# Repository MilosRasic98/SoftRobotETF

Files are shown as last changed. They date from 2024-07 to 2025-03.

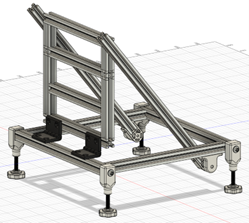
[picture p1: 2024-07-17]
Main Assembly/Frame/Pictures/FrameVertical.png

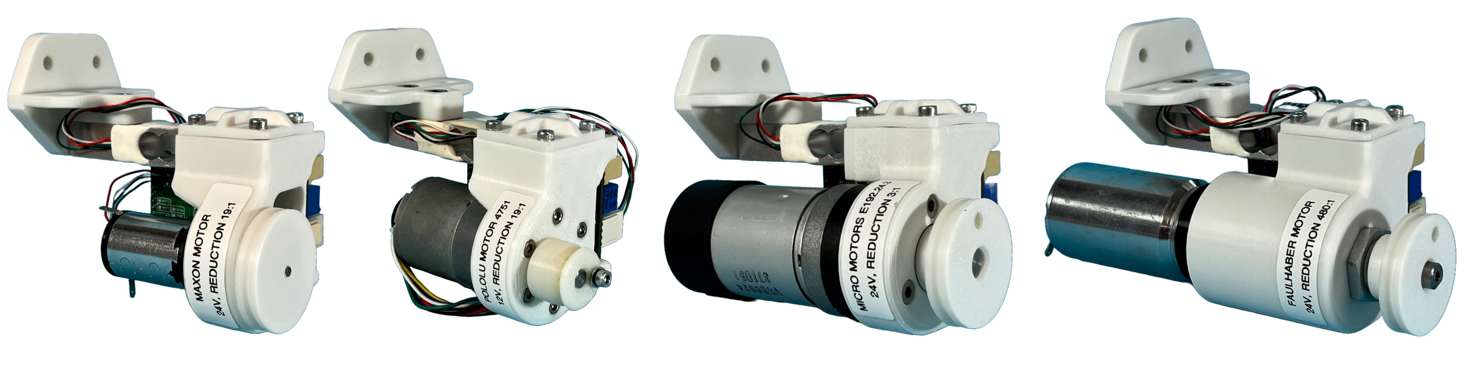
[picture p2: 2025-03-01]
Pictures/DifferentMotorSetups.png

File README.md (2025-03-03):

# Open Source Soft Robotics Platform - SoftRobotETF

This repository covers the complete development and testing of an open-source soft robotics platform developed at the School of Electrical Engineering, University of Belgrade in Serbia (https://www.etf.bg.ac.rs).

The main goal of this project was to develop a low-cost modular platform for testing different highly elastic soft robot continuum shapes and different actuator mechanisms. This platform was primarily used to test tendon-driven soft robots, both with internal and external tendon routing. This repository contains all of the necessary files for anyone to recreate this project. This includes:

1. Software for the Actuators, Robot Controller, and Python Scripts for controlling the Robot over Serial
2. Gerber files for the Actuator PCBs
3. CAD files for the actuators and the main soft robot construction
4. CAD files for 2 different silicone molds used for casting the soft robots

Besides this GitHub repository, there is a Google Sheet with the complete BOM for the Actuator PCB, known Errors, as well as the API and the implemented commands. You can find the sheet here: https://docs.google.com/spreadsheets/d/1j4l9SDbZnH_yYO-BC3xJZ4RkYJjM1L0_M2_zAHDFm0k/edit?usp=sharing

If you're trying to recreate a part of this project and you're stuck somewhere or some files are missing, feel free to contact me! Email: milosrasic98@gmail.com





To see how the robot looks in motion, click on the picture below, which will take you to the YouTube video, or click this link (https://www.youtube.com/watch?v=fuDRdF3EgcY)

IMAGE ALT TEXT HERE (https://www.youtube.com/watch?v=fuDRdF3EgcY)

## Requirement List

Before the development of this project, a requirement list was put together to guide the project in a single direction.

1. Ability to test different shapes and sizes of continuum shapes
2. Ability to test highly elastic soft robots
3. Precise force control tendon actuators
4. Multiple actuator setup

To satisfy the first two conditions, the frame of the robot was made using aluminium 20x20 extrustions. This enabled the maximum modularity and configurability of the system while still keeping everything sturdy. In this way, different actuators can be mounted using a few screws, and the same goes for different continuum shapes. 

Fig1_whitebackground_cropped

## Testing Different Shapes

To make the testing of different shapes even more straightforward, a plate and plate holder were designed and 3D printed so that different continuum shapes can easily be tested. In the pictures below, you can see the shape of the plate holder that attaches to the main frame. Soft robot bodies are cast with the plate attached to them and can then be easily attached to the plate holder with a couple of machine screws. This allows for easy testing of different continuum shapes by simply editing the CAD model of the plate to have the silicone anchors in the right places.

PlateWithDimensions

DifferentShapes

The plates shown above are designed for silicone continuums that are cast with the anchors inserted into the uncured silicone. Besides that, there are other options when using continuum shapes 3D printed out of TPU, for example. In the picure below, besides the silicone anchors, two additional methods can be seen for securing the continuum to the plate, one being with screws, and the other having a socket for glueing the continuum to the plate. 



## Testing Highly Elastic Soft Robots

While the shore hardness of the silicone above is high enough for the silicone robot to stand on its own in the vertical position, the idea with this platform was to enable testing silicone rubbers with lower shore hardnesses as well. For those cases, the silicone rubber wouldn't be able to support itself, so an addition to this platform is that the angle of the central part of the frame can be changed, and a simple holder for the silicone robot can be added, as shown in the picture below.

cropped_IMG_1597

## Actuators

A lot of time and effort was spent on the actuator design. The main goal for the actuators was, as stated above, to have precise force control. While current is directly proportional to the torque of the motor, the issue arises when the system needs to move from static to dynamic reference and vice versa, and also when there is a gearbox attached to the motor (sometimes with a lot of backlash). All of those things can cause issues with force control, which is why it was decided to measure the tendon force directly and close the control loop through the load cell measurement. The design of the final actuator is shown in the picture below.

ActuatorLabeledV2

A custom PCB was designed around the Raspberry Pi Pico as the MCU that controls a brushed DC motor using the DRV8842 motor driver. While a load cell is usually connected to an MCU using something like an HX711 24bit Sigma Delta ADC, this wasn't good enough for this use case since its maximum sample rate is 80SPS. Instead, the load cell was connected to an instrumentation amplifier, INA826, that could provide the necessary sample rate for the control loop. Since the amplification could be adjusted on the instrumentation amplifier using a potentiometer, a calibration method was needed to ensure accurate absolute measurements. This was done using a calibration stand that is described at the bottom of this Readme file. The gerber files for the PCB are available in the Actuators directory, and the PCB and electronics can be seen in the pictures below.

Outlook-PCB1 PNG

1-PowerElectronics

2-MotorController

3-LoadCell

4-RaspberryPico

The motors that are shown in all of the pictures above and that were used for all of the tests are the Pololu 12V motors with 19:1 reductors (https://www.pololu.com/product/2822). These aren't the motors that need to be used, however, because the design of the actuators allows the use of any brushed DC motor (Up to 28V and 5A) by redesigning a single 3D printable part. Different motor setups with the same electronics can be seen in the picture below.

DifferentMotorSetups

A single actuator can be used as a standalone unit by simply connecting a USB cable to the Raspberry Pi Pico. While this is easy to use for some simple tests, the goal was to be able to have multiple actuator setups. This is why both the hardware and software for these actuators were developed so that multiple of these actuators can be easily daisy-chained and controlled over I2C (Actuators have dual power connectors to enable daisy chaining, as well as multiple I2C connectors). In a multi-actuator setup, a Robot Controller Raspberry Pi Pico is needed that acts as the master device on the I2C bus.

The API for controlling the robot was designed to mimic the look of G Code commands, where a command number would be followed by space-separated parameters that are to be sent to the actuator(s). In a multi-actuator setup, these commands are sent to the Soft Robot Controller over Serial, which then translates those commands to I2C and sends them to all of the actuators. The Soft Robot Controller also plays a role in gathering the data from all of the actuators and from the IMU attached to the top of the robot. That data is saved into a CSV file and further analyzed after the tests are done. Some of the commands are shown in the table below

| Command | Name | Description | Command Format - Serial | Command Format - I2C | Parameters |
|---------|------|-------------|-------------------------|----------------------|------------|
| C0 | Stop All	| When the controller receives this command, it shuts down both PWM channels to 0% duty cycle, it disables the driver and turns off the enable LED | C0 | {0, 0, 0, 0, 0, 0, 0, 0, 0, 0, 0, 0, 0, 0, 0, 0} | None |
| C1 | Enable/Disable Driver (All) | When the controller receives this command, depending on the parameter, it will either enable or disable the driver, which will also be shown through the Enable LED on the PCB. Disabling the driver this way does not effect the PWM duty cycle like the C0 does |	C1 1/0 | {1, X, 0, 0, 0, 0, 0, 0, 0, 0, 0, 0, 0, 0, 0, 0} | X = 1 - Enable <br> X = 0 - Disable |
| C2 | Decay Mode | This command changes the decay mode on the DRV8842. For a detailed description of decay mode, refer to the datasheet of the DRV8842 motor driver. | C2 1/0 | {2, X, 0, 0, 0, 0, 0, 0, 0, 0, 0, 0, 0, 0, 0, 0} | X = 1 - Fast Decay <br> X = 0 - Slow Decay |
| C3 | Change Mode (All) | This command changes the mode of the actuator; in this way, the algorithm structure can be changed for the controller itself. <br> Mode 1 - Manual Control <br> Mode 2 - PI Controller Load Cell <br> Mode 3 - PI Controller IMU | C3 X | {3, X, 0, 0, 0, 0, 0, 0, 0, 0, 0, 0, 0, 0, 0, 0} | X - Mode X |
| C4 | Manual Drive | This command enables driving the motor in one or the other direction by setting the PWM duty cycle manually as well as the motor direction. For this command to work, the motor driver needs to be enabled first; the command will not automatically enable the motor driver. If the direction is set to 3, only the PWM will be changed with the before chosen direction. | C4 DX SY | {4, X, Y, 0, 0, 0, 0, 0, 0, 0, 0, 0, 0, 0, 0, 0} | X - Direction parameter [1, 2, 3] <br> X = 1 - Direction 1 <br> X = 2 - Direction 2 <br> X = 3 - Last direction <br> Y - Speed [0 - 100] <br> Y = Duty Cycle [%] |
| C5 | Set Force Reference | This command sets the reference of the PI Controller that closes its loop through the load cell. The reference is set in grams and can be anything between 0g and 10000g (0g to 1000g in safe mode). For I2C, the reference is calculated as: <br> Reference = 255 * X1 + X2 | C5 X | {5, X1, X2, 0, 0, 0, 0, 0, 0, 0, 0, 0, 0, 0, 0, 0} | X - Force reference [0-10000] <br> X = X1 * 255 + X2 |

The table above shows some of the commands. The full list of commands and future commands that will be added can be found in the Google Sheet: https://docs.google.com/spreadsheets/d/1j4l9SDbZnH_yYO-BC3xJZ4RkYJjM1L0_M2_zAHDFm0k/edit?usp=sharing

## Silicone Rubber

In the pictures above, two different silicone rubbers are shown. The pink silicone rubber is Mold Max 30 silicone (https://www.smooth-on.com/products/mold-max-30/), which was mixed as per the manufacturer's instructions and degassed in a vacuum chamber before being poured into a mold. The green silicone rubber was an experiment using natural silicone rubber mixed with food dye to speed up the curing process before being poured into the mold. For testing the properties of the different silicones, a manual strain test apparatus was constructed for measuring the tensile strength of the different silicone rubbers.



Results that were made using this apparatus are shown in the two figures below.

Silicone Rubber - Sample 1

Silicone Rubber - Force Change at 100 Elongation

CAD models for both of the molds can be found in the CAD directory. Since the plate had to stay attached to the silicone after taking it out of the mold. Special consideration was taken in designing these molds so that they can be disassembled around the soft robot, leaving the soft robot with the plates attached in the end.

ExplodedMold2

MoldFigureEdited

## Test Stand

As mentioned above, the actuator needs to be calibrated because the amplification of the instrumentation amplifier can be adjusted using a potentiometer. The calibration stand has a calibrated load cell at the top that is connected to the actuator using a tensioner and a spring. In this way, the force can be adjusted and kept at the desired force. The calibration stand and the calibration graph are shown in the pictures below.

CalibrationStand

Actuator Load Cell Calibration

## Results

This part will showcase some of the recorded results using this setup. The results shown here are with either one or two actuators, with an MPU6050 attached to the top of the robot. The measurements are done on the round Mold Max 30 silicone continuum. In the picture below, a sawtooth reference was sent to the actuator between 10N and 50N. This soft robot had internally routed tendons.

Reference Measurement - Test Segment - Sawtooth

The angle measured at the top of the robot is shown in the figure below.

Roll Angle - Test Segment - Sawtooth

By looking at a rising edge of the single peak, we can try estimating a linear function to approximate the angle based on the force, as shown in the picture below.

Angle Estimation Based on Force - Segment

Using the parameters of those lines, the comparison between the measured and estimated angles is shown in the figure below.

Roll Angle Measured and Estimated - Test Segment - Sawtooth

Using the parameters from the line calculated above, the estimated angle was calculated for a test where a sine reference was sent to the actuator.

Roll Angle Measured and Estimated - Full Test - Sine

The estimations weren't done for the two-actuator setup because there is coupling between the actuators; the actuators were placed at 90 degrees from each other. The results of those tests are shown below.

Reference Measurement - Test Segment

Pitch and Roll - Test Segment

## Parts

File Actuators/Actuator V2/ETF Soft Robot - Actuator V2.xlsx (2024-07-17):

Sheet: Document Outline
Document Description: |  |  | This document contains all of the relevant information needed for developing, testing and using the Soft Robot V1, as well as all of the relevant documentation like the BOM and the Pico Pinout. This document consists of multiple tabs, this first tab is used to outline the whole document as well as give a description of all tabs that are in this document.
Document Author: |  | Milos Rasic
Author Email: |  | milosrasic98@gmail.com
Table of Contents |  |  |  | Warnings
# | Tab Name | Tab Description |  | # | Name | Description
1 | PCB V1 Parts Sourcing | This tab contains the BOM for the PCB V1 as well as the designators for all components and locations where to buy them (if possible, Kelco was chosen as a supplier since they are local, if not, Farnell was used) |  | 1 | Low Number Command Checks | Because the inital version of the code checks the command code based on what it starts with, there is a possibility of treating a command like C10 for a C1 command, make sure that the character after the command code is a space.
2 | Error Log List | Error Log List contains the list of all errors that were noticed during soldering as well testing of the new PCB. This is also a place where new features or ideas can be written down for next iterations. |  | 2
3 | Pico Pinout | Pico Pinout contains a spreadsheet with connections for all of the pins on the Raspberry Pico as well as status for all of the pins have been they tested or not. |  | 3
4 | Commands | This tab contains the list of commands that can be used with the Soft Robot Controller, it includes their description, variants both for Serial and I2C communication, as well as examples and parameters descriptions. |  | 4
5 | LED Reading Manual | This tab shows how to read the different signals given by the LEDs on the actuator |  | 5
6 | Actuator Calibartion | All of the collected measurements used for getting values in grams from raw ADC values |  | 6
7 | Actuator Info | Contains all of the relevant info and parameters for each of the actuators |  | 7
8 | Wiring Diagrams | All of the important wiring diagrams which need additional clarification |  | 8
9 |  |  |  | 9
10 |  |  |  | 10
11 |  |  |  | 11
12 |  |  |  | 12
13 |  |  |  | 13
14 |  |  |  | 14
15 |  |  |  | 15
16 |  |  |  | 16
17 |  |  |  | 17
18 |  |  |  | 18
19 |  |  |  | 19
20 |  |  |  | 20

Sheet: PCB V1 Parts Sourcing
Tab Description: |  | This tab represents the BOM for the PCB V1, it includes numbers needed for each PCB as well as the designators, besides that each part is linked at least to one store, if possible, parts were sourced from Kelco since they are the local supplier with the biggest inventory of SMD components, while for most other things, the chosen supplier was Farnell.
# | Name | Designator | Store | Qty per Board | Description | Alternative | Link | Part of Circuit | Number Ordered | Status | ID
1 | TSP54331DR | U6 | Farnell | 1 | Buck Chip | X | https://export.farnell.com/texas-instruments/tps54331dr/dc-dc-conv-buck-570khz-soic-8/dp/3121757?st=buck | Power Supply | 3+3 | Arrived | SMD-B2-R2C1
2 | SDR0604-6R8ML | D1 | Farnell | 1 | Power Inductor | X | https://export.farnell.com/bourns/sdr0604-6r8ml/inductor-6-8uh-2-5a-smd/dp/1828001 | Power Supply | 5+5 | Arrived | SMD-B2-R1C1
3 | B340A-13-F | D2, D3 | Farnell | 2 | Schottky Diode | X | https://export.farnell.com/multicomp-pro/b340a-13-f/diode-rectifier-3a-40v-do-214ac/dp/2306401?st=b340a | Power Supply | 10 | Arrived | SMD-B1-R3C5
4 | 08056D476MAT2A | C1, C2, C3, C10, C20, C21 | Farnell | 6 | 4.7uF Cap | X | https://export.farnell.com/kyocera-avx/08056d476mat2a/cap-47uf-6-3v-x5r-0805/dp/4164100 | All Schematics | 30 | Arrived | SMD-B1-R1C5
5 | MCWR06X2942FTL | R1 | Farnell | 1 | 29k4 Resistor | X | https://export.farnell.com/multicomp/mcwr06x2942ftl/res-29k4-1-0-1w-0603-thick-film/dp/2694813 | Power Supply | 20 | Arrived | SMD-B1-R2C6
6 | 100nF Cap | C4, C6, C7, C11, C13, C16, C17, C18, C19, C22, C23 | Kelco | 11 | 100nF Cap 0603 | X | https://kelco.rs/katalog/detalji.php?ID=11061 | All Schematics | 100 | Arrived | SMD-B1-R1C4
7 | 10nF Cap | C5, C12 | Kelco | 2 | 10nF Cap 0603 | X | https://kelco.rs/katalog/detalji.php?ID=11586 | All Schematics | 100 | Arrived | SMD-B1-R1C3
8 | 1nF Cap | C8 | Kelco | 1 | 1nF Cap 0603 | X | https://kelco.rs/katalog/detalji.php?ID=10781 | Power Supply | 100 | Arrived | SMD-B1-R1C2
9 | 47pF Cap | C9 | Kelco | 1 | 47pF Cap | X | https://kelco.rs/katalog/detalji.php?ID=12902 | Power Supply | 100 | Arrived | SMD-B1-R1C1
10 | 15k Resistor | R2, R4, R5 | Kelco | 3 | 15k Resistor | X | https://kelco.rs/katalog/detalji.php?ID=13740 | All Schematics | 100 | Arrived | SMD-B1-R2C5
11 | 4k7 Resistor | R3, R16, R17, R22, R23 | Kelco | 5 | 4k7 Resistor | X | https://kelco.rs/katalog/detalji.php?ID=11708 | All Schematics | 100 | Arrived | SMD-B1-R2C3
12 | DRV8842 | U5 | Farnell | 1 | DC Motor Driver | X | https://export.farnell.com/texas-instruments/drv8842pwp/stepper-motor-driver-5a-28htssop/dp/3005858?st=dc%20motor%20driver | Motor Driver | 3+3 | Arrived | SMD-B2-R2C2
13 | WW06PR750FTL | R9, R10, R11, R12, R13 | Farnell | 5 | Current Sense Resistor | X | https://export.farnell.com/walsin/ww06pr750ftl/res-0r75-1-50v-0603-thick-film/dp/2503092 | Motor Driver | 30 | Arrived | SMD-B1-R2C1
14 | 2850090 | F1 | Farnell | 1 | Fuse 5A | Fuse 2A | https://export.farnell.com/multicomp/mccfb2410ttt-c-5/fuse-smd-5a-slow-blow-2410/dp/2850090 | Power Supply | 2+5 | Arrived | SMD-B2-R1C7
15 | INA826 | U7 | Farnell | 1 | Instrumentation Amp | X | https://export.farnell.com/texas-instruments/ina826aidgk/ic-amp-instr-8msop/dp/3004514 | Sense Circuit | 2+3 | Arrived | SMD-B1-R2C3
16 | 680R 0603 | R18, R19, R20, R21, R24 | Kelco | 5 | 680R 0603 - LED Resistor | X | https://kelco.rs/katalog/detalji.php?ID=14179 | All Schematics | 100 | Arrived | SMD-B1-R2C2
17 | 5k6 0603 | R6, R7 | Kelco | 2 | 5k6 0603 Resistor | X | https://kelco.rs/katalog/detalji.php?ID=11709 | Motor Driver | 100 | Arrived | SMD-B1-R2C4
18 | 1M 0603 | R8 | Kelco | 1 | 1M 0603 Resistor | X | https://kelco.rs/katalog/detalji.php?ID=13744 | Motor Driver | 10 | Arrived | SMD-B1-R2C7
19 | 100uF Electrolytic Cap | C14, C15 | Kelco | 2 | 100uF Electrolytic Cap | X | https://kelco.rs/katalog/detalji.php?ID=9985 | All Schematics | 15 | Arrived | ALL-B3-R1C3
20 | Trim Pot 100R | R14, R15 | Kelco | 2 | Trim Pot 100R | X | https://kelco.rs/katalog/detalji.php?ID=9990 | Sense Circuit | 10 | Arrived | ALL-B3-R1C4
21 | Trim Pot 20R |  | TODO |  | Trim Pot 20R | X | TODO |  | 10 | Need to Buy | ALL-B3-R1C5
22 | Red LED | LED1, LED2, LED3, LED4, LED5, LED6 | Kelco | 6 | Red LED 0603 | X | https://kelco.rs/katalog/detalji.php?ID=18012 | All Schematics | 20 | Arrived | SMD-B1-R3C1
23 | Green LED |  | Kelco |  | Green LED 06033 | X | https://kelco.rs/katalog/detalji.php?ID=18013 | All Schematics | 20 | Arrived | SMD-B1-R3C2
24 | Blue LED |  | Kelco |  | Blue LED 0603 | X | https://kelco.rs/katalog/detalji.php?ID=17592 | All Schematics | 10 | Arrived | SMD-B1-R3C3
25 | Pink LED |  | Kelco |  | Pink LED 0603 | X | https://kelco.rs/katalog/detalji.php?ID=17568 | All Schematics | 10 | Arrived | SMD-B1-R3C4
26 | Power Connector PCB | J1, J2 | Kelco | 2 | Power Connector PCB | X | https://kelco.rs/katalog/detalji.php?ID=12651 | Power Supply | 10 | Arrived | ALL-B3-R1C1
27 | Power Connector Cable |  | Kelco |  | Power Connector Cable | X | https://kelco.rs/katalog/detalji.php?ID=12721 | Power Supply | 4 | Arrived | ALL-B3-R1C2
28 | Raspberry Pico | MCU1 | Farnell | 1 | Raspberry Pico Microcontroller | Raspberry Pico W | https://export.farnell.com/raspberry-pi/raspberry-pi-pico/raspberry-pi-32bit-arm-cortex/dp/3643332 | Microcontroller | 2 | Arrived | ALL-B3-R2C1
29 | Female Headers 2.54 | PIN1 | Kelco | X | Female header pins | X | https://kelco.rs/katalog/detalji.php?ID=18882 | All Schematics | 10 | Arrived | ALL-B3-R3C1
30 | Male Header 2.54 | PIN2 | Kelco | X | Male header pins | X | https://kelco.rs/katalog/detalji.php?ID=7923 | All Schematics | 3 | Arrived | ALL-B3-R3C2
31 | Nylon Connector 4P PCB | NYL1, NYL2, NYL3, NYL4, NYL5 | Kelco | 5 | Nylon Connector 4P PCB | X | https://kelco.rs/katalog/detalji.php?ID=7918 | All Schematics | X | In Stock | ALL-B3-R2C4
32 | Nylon Connector 4P Cable |  | Kelco |  | Nylon Connector 4P Cable | X | https://kelco.rs/katalog/detalji.php?ID=7913 |  | X | In Stock | ALL-B3-R1C6
33 | Nylon Connector Pins |  | Kelco |  | Nylon Connector Pins | X | https://kelco.rs/katalog/detalji.php?ID=14868 |  | X | In Stock | TODO
34 | INA125P | U1 | Kelco | 1 | Instrumentation Amp | X | https://kelco.rs/katalog/detalji.php?ID=21799 | Sense Circuit | X | Need to Buy | TODO
35 | DIP16 Socket | U1_SOCKET | Kelco | 1 | Socket for DIP16 | X | TODO | Sense Circuit | X | Need to Buy | ALL-B3-R2C2
36 | Male Header 2x2.54 | PIN3 | Kelco | X | Pins for the jumpers | X | https://kelco.rs/katalog/detalji.php?ID=10308 | All Schematics | X | Need to Buy | ALL-B3-R2C3
37 | Jumpers | PIN4 | Kelco | X | Jumpers for selecting settings | X | https://kelco.rs/katalog/detalji.php?ID=16633 | All Schematics | X | Need to Buy | TODO
38
39
40
41
42
43
44
45
46
47
48
49
50

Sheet: Error Log List
Tab Description: |  | This tab represents the Error and Idea log that will be updated through the development and the testing process.
# | Error Name | Error Type | Error/Idea Description | Proposed Solution | Board Version | Date | Importance | Urgency | Status
1 | Inductor Footprint | PCB | The footprint that was used for the inductor is too small. | Either correct the footprint on the PCB, or if possible, find an alternative inductor that has the matching footprint to the current one. | V1 | 17.12.2023 | Critical | Non Urgent | Not Solved
2 | Electrolyric Cap Footprint | PCB | The footprint that was used for the eletrolytic capacitor is a bit on the smaller side making it hard to solder the capacitor properly to the PCB. | Try using a smaller capactior (smaller ones are just rated to a lower voltage, the current one is rated up to 50V), or use a different footprint for the capacitor. | V1 | 17.12.2023. | Non Critical | Non Urgent | Not Solved
3 | 3V3 LED too bright | Schematic | The 3V. power LED is too bright when used with a 680R resistor. | Try using 1k-2k until the desired brightness is achieved | V1 | 17.12.2023. | Non Critical | Non Urgent | Not Solved
4 | Silkscreen missmatch C10 | PCB | Silkscreen on the PCB for C10 and C11 have been swapped around | Fix the silk screen in EasyEDA | V1 | 17.12.2023. | Non Critical | Non Urgent | Not Solved
5 | Pico Caps to bottom | PCB | Capacitors used for the Raspberry Pico are too close to the female box connected of the Raspberry Pico. | There is a lot of space underneath the pico (bottom layer), move the capacitors to the bottom layer to make the soldering easier | V1 | 17.12.2023. | Non Critical | Non Urgent | Not Solved
6 | Encoder divider resistors to bottom | PCB | The voltage divider resistors used for the encoder are underneath the Pico on the top layer, making them hard to solder and work on once the Pico is in place. | Consider moving the resistors to the bottom layer if there is enough room for tracks. | V1 | 17.12.2023. | Non Critical | Non Urgent | Not Solved
7 | PCB ID | Idea / Feature | Distinguish between different PCB-s within the same batch. | Add a silkscreen place (rectangle or something similar) where a sticker could be put with the ID of the PCB. | V1 | 17.12.2023. | Non Critical | Non Urgent | Not Solved
8 | I2C Address | Idea / Feature | Physical way of changing the I2C address on the Raspberry Pico | Add a DIP switch to easily change the I2C address on each PCB | V1 | 17.12.2023. | Non Critical | Non Urgent | Not Solved
9
10
11
12
13
14
15
16
17
18
19
20
21
22
23
24
25
26
27
28
29
30
31
32
33
34
35
36
37
38
39
40
41
42
43
44
45
46
47
48
49
50
51
52
53
54
55
56
57
58
59
60
61
62
63
64
65
66
67
68
69
70
71
72
73
74
75
76
77
78
79
80
81
82
83
84
85
86
87
88
89
90
91
92
93
94
95
96
97
98
99
100

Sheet: Pico Pinout
Tab Description: |  | This tab represents the pinout of the Pico and how it's connected to everything on the PCB V1, it shows all of the pins, the connections as well as if that pin feature has been tested/implemented yet.
Status | Pin Purpose | Pin Connection | GPIO | Pin Number | Pin Number | GPIO | Pin Connection | Pin Purpose | Status
Unused | NC | NC | GPIO0 | 1 | 40 | X | NC | NC | Unused
Unused | NC | NC | GPIO1 | 2 | 39 | X | NC | NC | Unused
Done | GND | GND | GND | 3 | 38 | GND | GND | GND | Done
Needs Testing | PWM for controlling the spin of the motor in one direction | MOTOR_CTRL_1 | GPIO2 | 4 | 37 | X | NC | NC | Unused
Needs Testing | Changes the decay mode for the DRV8842, HIGH is fast decay, LOW is slow decay | MOTOR_DECAY | GPIO3 | 5 | 36 | X | 3V3 | Input Power from buck - 3V3 | Done
Needs Testing | PWM for controlling the spin of the motor in the other direction | MOTOR_CTRL_2 | GPIO4 | 6 | 35 | X | NC | NC | Unused
Needs Testing | Fault signal from the motor driver | MOTOR_FAULT | GPIO5 | 7 | 34 | GPIO28 | LOAD_CELL_INA826 | Input signal from the load cell that is connected to the INA826 | Needs Testing
Done | GND | GND | GND | 8 | 33 | GND | GND | GND | Done
Needs Testing | Signal for putting the motor driver to sleep | MOTOR_SLEEP | GPIO6 | 9 | 32 | GPIO27 | LOAD_CELL_INA125 | Input signal from the load cell that is connected to the INA125 | Needs Testing
Needs Testing | Signal for reseting the motor driver | MOTOR_RESET | GPIO7 | 10 | 31 | GPIO26 | MOTOR_CURRENT | Input analog signal from the motor driver for measuring the current consumption of the motor | Needs Testing
Done | Signal for the Heartbeat LED, pulses at 1Hz in normal operation, in error state switches to 5Hz | LED_HEARTBEAT | GPIO8 | 11 | 30 | X | NC | NC | Unused
Unused | Encoder A input signal from the motor | ENC_A | GPIO9 | 12 | 29 | GPIO22 | GPIO_22 | Not used | Unused
Done | GND | GND | GND | 13 | 28 | GND | GND | GND | Done
Unused | Encoder B input signal from the motor | ENC_B | GPIO10 | 14 | 27 | GPIO21 | I2C_SCL | I2C communication with the master controller | Needs Testing
Done | Signal for the Fault LED which shows if there is a fault reported by the motor driver | LED_DRV_FAULT | GPIO11 | 15 | 26 | GPIO20 | I2C_SDA | I2C communication with the master controller | Needs Testing
Done | Signal for the Enable LED, this LED shows if the power electronics have been enabled for the motor | LED_DRV_EN | GPIO12 | 16 | 25 | GPIO19 | SPI0_MOSI | Not used | Unused
Done | Signal for the Mode LED, which shows which type of software driver is currently enabled, can be configured for anything else as well | LED_CTRL_MODE | GPIO13 | 17 | 24 | GPIO18 | SPI0_CLK | Not used | Unused
Done | GND | GND | GND | 18 | 23 | GND | GND | GND | Done
Needs Testing | Connection to the HX711 for the calibration stand | HX711_SCK | GPIO14 | 19 | 22 | GPIO17 | SPI0_CSN | Not used | Unused
Needs Testing | Connection to the HX711 for the calibration stand | HX711_DT | GPIO15 | 20 | 21 | GPIO16 | SPI0_MISO | Not used | Unused
Legend
Done | Everything works as expected
Needs Testing | Still not tested and implemented
Unused | Not used for now, needs testing before use
Not Working | Testing failed

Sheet: Commands
Tab Description: |  | This tab represents all of the commands that can be used with the Soft Robot Actuator as well as their formats, descriptions, examples and parameters descriptions.
# | Command Code | Name | Description | Command Format - Serial | Command Example - Serial | Command Format - I2C | Command Example - I2C | Parameters | Status
0 | C0 | Stop All | When the controller receives this command, it shuts down both PWM channels to 0% duty cycle, it disables the driver and turns off the enable LED | C0 | C0 | {0, 0, 0, 0, 0, 0, 0, 0, 0, 0, 0, 0, 0, 0, 0, 0} | {0, 0, 0, 0, 0, 0, 0, 0, 0, 0, 0, 0, 0, 0, 0, 0} | None | Done
1 | C1 | Enable/Disable Driver | When the controller receives this command, depending on the parameter, it will either enable or disable the driver, which will also be shown through the Enable LED on the PCB. Disabling the driver this way does not effect the PWM duty cycle like the C0 does | C1 1/0 | C1 1 - Enable Driver C1 0 - Disable Driver | {1, X, 0, 0, 0, 0, 0, 0, 0, 0, 0, 0, 0, 0, 0, 0} | {1, 1, 0, 0, 0, 0, 0, 0, 0, 0, 0, 0, 0, 0, 0, 0} - Enable {1, 0, 0, 0, 0, 0, 0, 0, 0, 0, 0, 0, 0, 0, 0, 0} - Disable | X = 1 - Enable X = 0 - Disable | Done
2 | C2 | Decay Mode | This command changes the decay mode on the DRV8842. For a detailed description of decay mode refer to the datasheet of the DRV8842 motor driver. | C2 1/0 | C2 1 - Fast Decay Mode C2 0 - Slow Decay Mode | {2, X, 0, 0, 0, 0, 0, 0, 0, 0, 0, 0, 0, 0, 0, 0} | {2, 1, 0, 0, 0, 0, 0, 0, 0, 0, 0, 0, 0, 0, 0, 0} - Fast Decay {2, 0, 0, 0, 0, 0, 0, 0, 0, 0, 0, 0, 0, 0, 0, 0} - Slow Decay | X = 1 - Fast Decay X = 0 - Slow Decay | Done
3 | C3 | Change Mode | This command changes the "mode" of the actuator, in this way, algorithm structure can be changed for the controller itself. Mode 1 - Manual Control Mode 2 - PI Controller Load Cell Mode 3 - PI Controller IMU | C3 X | C3 1 - Switch to Mode 1 C3 2 - Switch to Mode 2 | {3, X, 0, 0, 0, 0, 0, 0, 0, 0, 0, 0, 0, 0, 0, 0} | {3, 1, 0, 0, 0, 0, 0, 0, 0, 0, 0, 0, 0, 0, 0, 0} - Mode 1 {3, 2, 0, 0, 0, 0, 0, 0, 0, 0, 0, 0, 0, 0, 0, 0} - Mode 2 | X - Mode X | Done
4 | C4 | Manual Drive | This command enables driving the motor in one or the other direction by setting the PWM duty cycle manually as well as the motor direction. For this command to work, the motor driver needs to be enabled first, the command will not automatically enable the motor driver. If the direction is set to 3, only the PWM will be changed with the before chosen direction. | C4 DX SY | C4 D1 S50 - Direction 1 Speed 50 C4 D2 S90 - Direction 2 Speed 90 | {4, X, Y, 0, 0, 0, 0, 0, 0, 0, 0, 0, 0, 0, 0, 0} | {4, 1, 50, 0, 0, 0, 0, 0, 0, 0, 0, 0, 0, 0, 0, 0} - Dir 1 Speed 50 {4, 2, 90, 0, 0, 0, 0, 0, 0, 0, 0, 0, 0, 0, 0, 0} - Dir 0 Speed 90 | X - Direction parameter [1, 2, 3] X = 1 - Direction 1 X = 2 - Direction 2 X = 3 - Last direction Y - Speed [0 - 100] Y = Duty Cycle [%] | Done
5 | C5 | Set Force Reference | This command sets the reference of the PI Controller that closes its loop through the load cell. The reference is set in grams and can be anything between 0g and 10000g (0g to 1000g in safe mode). For I2C, the reference is calculated as Reference = 255 * X1 + X2 | C5 X | C5 1250 - Set reference to 1250g | {5, X1, X2, 0, 0, 0, 0, 0, 0, 0, 0, 0, 0, 0, 0, 0} | {5, 4, 230, 0, 0, 0, 0, 0, 0, 0, 0, 0, 0, 0, 0, 0} - Set reference to 1250g | X - Force reference [0-10000] X = X1 * 255 + X2 | Done
6 | C6 | Reset Force Controller | This command resets the accumulator of the load cell PI controller. | C6 | C6 | {6, 0, 0, 0, 0, 0, 0, 0, 0, 0, 0, 0, 0, 0, 0, 0} | {6, 0, 0, 0, 0, 0, 0, 0, 0, 0, 0, 0, 0, 0, 0, 0} | None | Need to Implement
7 | C7 | Safe Mode | This puts the whole controller into Safe Mode, which limits the PWM to 25% duty cycle, it also puts a limit on the reference of 1000g and enables safe mode failsafe, that shuts down the driver if the load cell is detected to be over 1000g. | C7 | C7 | {7, 0, 0, 0, 0, 0, 0, 0, 0, 0, 0, 0, 0, 0, 0, 0} | {7, 0, 0, 0, 0, 0, 0, 0, 0, 0, 0, 0, 0, 0, 0, 0} | None | Need to Implement
8 | C8 | Save Parameters | Save all of the editable parameters to the flash memory of the Pico | C8 | C8 | {8, 0, 0, 0, 0, 0, 0, 0, 0, 0, 0, 0, 0, 0, 0, 0} | {8, 0, 0, 0, 0, 0, 0, 0, 0, 0, 0, 0, 0, 0, 0, 0} | None | Research
9 | C9 | Change Force Controller Parameters | With this command, change the Kp and Ki parameters of the load cell PI controller | C9 KP KI | C9 0.1 0.005 | TODO | TODO | TODO | Research
10 | C10 | Reset All Errors | Using this command, reset any errors that have happened on the controller | C10 | C10 | {10, 0, 0, 0, 0, 0, 0, 0, 0, 0, 0, 0, 0, 0, 0, 0} | {10, 0, 0, 0, 0, 0, 0, 0, 0, 0, 0, 0, 0, 0, 0, 0} | None | Done
11 | C11 | Enable/Disable Overcurrent Protection | Through current sense resistors, the DRV8842 can measure current and the Pico reads that using an analog pin. This command can enable or disable the overcurrent protection. If the overcurrent protection is enabled and the measured current goes above the overcurrent protection limit, the Pico will disable the driver, kill the PWM and go into error state. | C11 1/0 | C11 1 - Enable OC C11 0 - Disable OC | {11, X, 0, 0, 0, 0, 0, 0, 0, 0, 0, 0, 0, 0, 0, 0} | {11, 1, 0, 0, 0, 0, 0, 0, 0, 0, 0, 0, 0, 0, 0, 0} - Enable OC {11, 0, 0, 0, 0, 0, 0, 0, 0, 0, 0, 0, 0, 0, 0, 0} - Disable OC | X = 1 - Enable OC X = 0 - Disable OC | Need to Implement
12 | C12 | Set Overcurrent Protection Limit | Set the limit in mA at which the OC protection is triggered. This value can go anywhere from 0 to 3000mA, keep in mind the strength of the fuse that is currently installed on the PCB | C12 X | C12 1250 - Set OC limit at 1250mA | {12, X1, X2, 0, 0, 0, 0, 0, 0, 0, 0, 0, 0, 0, 0, 0} | {12, 4, 230, 0, 0, 0, 0, 0, 0, 0, 0, 0, 0, 0, 0, 0} - Set OC limit at 1250mA | X - OC Current Limit [0-3000] X = X1 * 255 + X2 | Need to Implement
13 | C13 | Live Serial Data | Toggle the live stream of all of the measured data on the actuator using this command, the only argument for the command is 1/0 that let's the user either enable or disable the data stream. | C13 1/0 | C13 1 - Enable Serial Data Stream C13 0 - Disable Serial Data Stream | {13, X, 0, 0, 0, 0, 0, 0, 0, 0, 0, 0, 0, 0, 0, 0} | {13, 1, 0, 0, 0, 0, 0, 0, 0, 0, 0, 0, 0, 0, 0, 0} - Enable {13, 0, 0, 0, 0, 0, 0, 0, 0, 0, 0, 0, 0, 0, 0, 0} - Disable | X = 1 - Enable X = 0 - Disable | Need to Implement
14 | C14
15 | C15
16 | C16
17 | C17
18 | C18
19 | C19
20 | C20
21 | C21
22 | C22
23 | C23
24 | C24
25 | C25
26 | C26
27 | C27
28 | C28
29 | C29
30 | C30
31 | C31
32 | C32
33 | C33
34 | C34
35 | C35
36 | C36
37 | C37
38 | C38
39 | C39
40 | C40
41 | C41
42 | C42
43 | C43
44 | C44
45 | C45
46 | C46
47 | C47
48 | C48
49 | C49
50 | C50

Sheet: LED Reading Manual
Tab Description: |  | This tab represents the BOM for the PCB V1, it includes numbers needed for each PCB as well as the designators, besides that each part is linked at least to one store, if possible, parts were sourced from Kelco since they are the local supplier with the biggest inventory of SMD components, while for most other things, the chosen supplier was Farnell.
# | LED Name | LED Description | Reading Manual | Troubleshooting
1 | 12V | The 12V LED indicates if the 12V power is coming to the board (after fuse). | If the LED is ON that means that 12V is coming into the system, if it's OFF that means that 12V is not coming into the system. | If the LED is OFF and you think it should be ON (Turned on PSU, everything connected), check if the fuse is okay, after that check the actual voltage on the board with the mutlimeter.
2 | 3V3 | The 3V3 LED indicated if the 3V3 rail is at a 3.3V level. | If the LED is ON, there is power on the 3V3 rail, if it's OFF there is no power on the 3V3 rail. | 3V3 LED can be ON and the 12V OFF only if the board is getting power from either the USB cable or from one of the I2C connectors. If the 3V3 LED is OFF and the 12V LED is ON, measure the 3V3 rail voltage with a multimeter, if the reading is bad, check the buck converter.
3 | HBEAT | The HBEAT LED shows the general state of the controller. | In normal operation the HBEAT LED should turn ON for 1 second and then turn OFF for 1 second, if it's in error mode, it will start blinking much faster. If the LED is just glowing solid green, that means that the MCU got stuck. | If reseting the board doesn't help, connect the USB Cable and check the Serial port for any help. Make sure to change the SERIAL_DEBUG parameter to true in the code.
4 | FAULT
5 | ENABLE
6 | MODE

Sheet: Actuator Calibration
Tab Description: |  | This Tab represents the calibration data gathered during the calibration process of the actuators, based on this data, parameters are calculated to convert the RAW ADC values into grams that are used for controlling the robot.
Process Description |  | The calibration process is done using the calibration stand. To begin, the actuator is loaded to the max desired value (for example 5000g/50N), this load is checked using the calibration stand load cell and HX711 amplifier. Turning the potentiometer for the INA826 we adjust the gain, our goal is to adjust the gain so that when everything is loaded to 5000g in our case, the INA826 can still go a bit higher to handle any overshoots. The maximum ADC value that can be read from the INA826 is around 2250 (check this number), since the INA826 is powered through 3V3 at 12bit ADC resolution.
Actuator 1 |  |  |  | Calculated best line using LMS |  | Calculated Series |  |  | Calibration Graph
# | Target Weight [g] | Load Scale - Measured | Load Scale - Raw ADC Reading [12bit] |  |  | Measured | Calculated | Delta
1 | 0 | -1 | 28 | y = 2.2629x + 1.33955 |  | 0 | 64.70075 | 64.70075
2 | 100 | 104 | 40 | k | 2.2629 | 104 | 91.85555 | 12.14445
3 | 200 | 204 | 83 | n | 1.33955 | 204 | 189.16025 | 14.83975
4 | 500 | 499 | 213 |  |  | 499 | 483.33725 | 15.66275
5 | 1000 | 1005 | 442 |  |  | 1005 | 1001.54135 | 3.45865
6 | 1500 | 1512 | 660 |  |  | 1512 | 1494.85355 | 17.14645
7 | 2000 | 2008 | 880 |  |  | 2008 | 1992.69155 | 15.30845
8 | 2500 | 2505 | 1100 |  |  | 2505 | 2490.52955 | 14.47045
9 | 3000 | 3014 | 1340 |  |  | 3014 | 3033.62555 | 19.62555
10 | 3500 | 3520 | 1555 |  |  | 3520 | 3520.14905 | 0.14905
11 | 4000 | 4001 | 1765 |  |  | 4001 | 3995.35805 | 5.64195
12 | 4500 | 4503 | 1990 |  |  | 4503 | 4504.51055 | 1.51055
13 | 5000 | 5002 | 2215 |  |  | 5002 | 5013.66305 | 11.66305

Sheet: Actuator Info
Tab Description: |  | This tab contains all of the relevant info and parameters for each of the actuators like I2C IDs, PI parameters, etc.
Actuators | I2C ID | Known Issues | INA826 k parameter | INA826 n parameter | Kp | Ki | Code Version
Actuator 1 | 0x11 | None | 2.2629 | 1.33955
Actuator 2 | 0x22 | None
Actuator 3 | 0x33 | None
Actuator 4 | 0x44 | None

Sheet: Wiring Diagrams
Tab Description: |  | This tab contains all of the wiring diagrams which require additional clarification
List of Wiring Diagrams
# | Diagram Name | Diagram Description | Number of conductors | Connections | Connector Side 1 | Connector Side 1 Picture | Connector Side 1 Link | Pinout Side 1 | Connector Side 2 | Connector Side 2 Picture | Connector Side 2 Link | Pinout Side 2 | Original Color Coded Wiring
1 | Main I2C Cable - from soft robot input connector to the first actuator | This is the cable that connects the input I2C connector on the Soft Robot with the first in line actuator on the soft robot. The wiring includes 3 signals, 2 for I2C and a common ground. Make sure that one of the actuators has jumpers for the I2C pull-ups in place for the I2C network to work properly. | 3 | 1. GND 2. I2C SCL 3. I2C SDA | Nylon 4 pin connector - Actuator side, only 3 pins used |  | https://www.kelco.rs/katalog/detalji.php?ID=7913 | As shown in the picture, the pinout from left to right: 1. GND 2. I2C SDA 3. I2C SCL 4. 3V3 | 3.5mm female connector |  | https://www.kelco.rs/katalog/detalji.php?ID=6109 | As shown in the picture: 1. Bigger Middle Pin - GND 2. Square Pin - I2C SCL 3. Round Pin - I2C SDA | The original cable used between these 2 connectors has the next color coding: 1. Black - GND 2. Blue - I2C SCL 3. Brown - I2C SDA
2 | I2C Daisy Chain Cable - between 2 actuators | This is the cable that goes between 2 actuators so they can all be on the same I2C bus. | 3 | 1. GND 2. I2C SCL 3. I2C SDA | Nylon 4 pin connector - Actuator side, only 3 pins used |  | https://www.kelco.rs/katalog/detalji.php?ID=7913 | As shown in the picture, the pinout from left to right: 1. GND 2. I2C SDA 3. I2C SCL 4. 3V3 | Nylon 4 pin connector - Actuator side, only 3 pins used |  | https://www.kelco.rs/katalog/detalji.php?ID=7913 | As shown in the picture, the pinout from left to right: 1. GND 2. I2C SDA 3. I2C SCL 4. 3V3 | The original cable used between these 2 connectors has the next color coding: 1. Black - GND 2. Blue - I2C SCL 3. Brown - I2C SDA
3 | Main Power Cable - from PSU to emergency stop button
4 | Primary Power Cable - from emergency button to first actuator
5 | Daisy Chain Power Cable - between 2 actuators
6 | MPU6050 Cable - between IMU and an actuator
7 | Load Cell Actuator Cable - between the actuator load cell and the actuator PCB
8 | Motor Cable - between the motor and the actuator PCB
9 | Calibration Stand HX711 Cable - between the calibration stand HX711 and the actuator
10 | Calibration Stand Load Cell Cable - between the calibration stand load cell and the HX711 amplifier

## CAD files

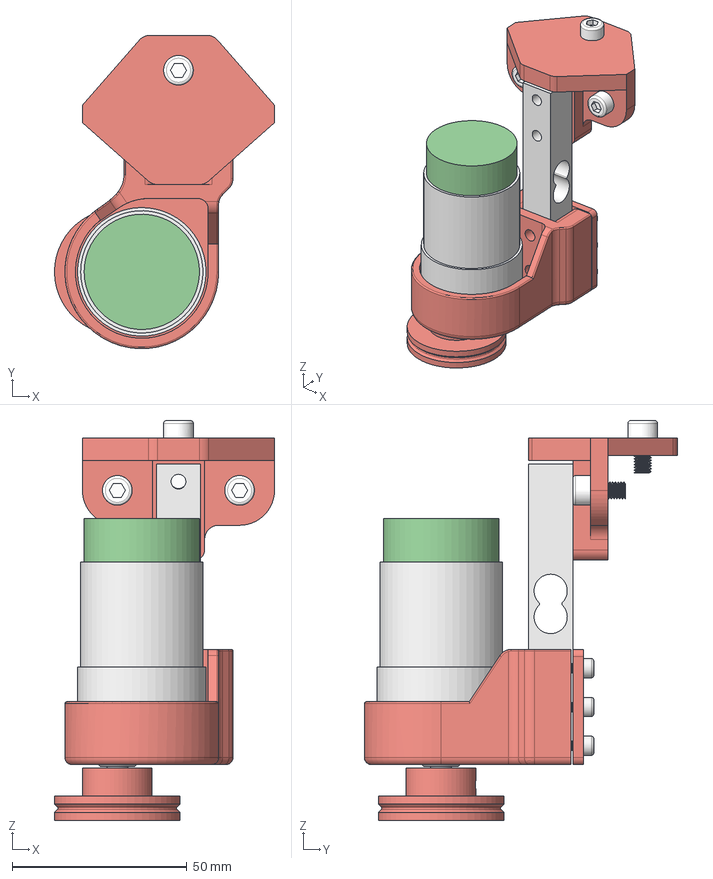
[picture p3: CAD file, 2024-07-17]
Actuators/Actuator V1 - Dual Motor Actuator/CAD models/Full Assembly/Full Motor Assembly V1.1.step
63.0 x 89.7 x 114.5 mm
Load Cell Mount V1
Pulley V1
M3x6mm x 12
Motor Mount
Additional Motor Brace
Load Cell
Pololu 1442 Geared DC Motor
M5x10mm x 5

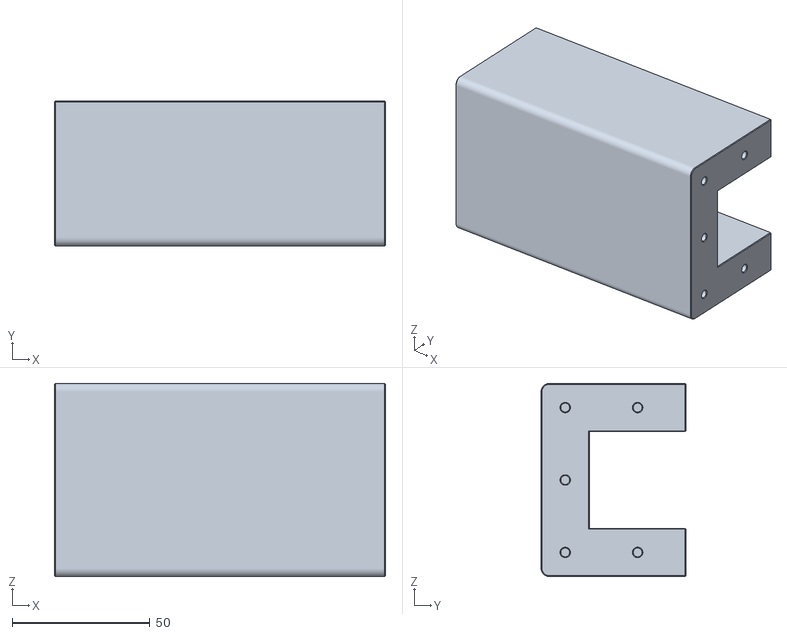
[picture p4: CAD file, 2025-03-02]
CAD/Square Silicone Rubber Mold/Main Center Mold Piece.stl
120.0 x 52.5 x 70.0

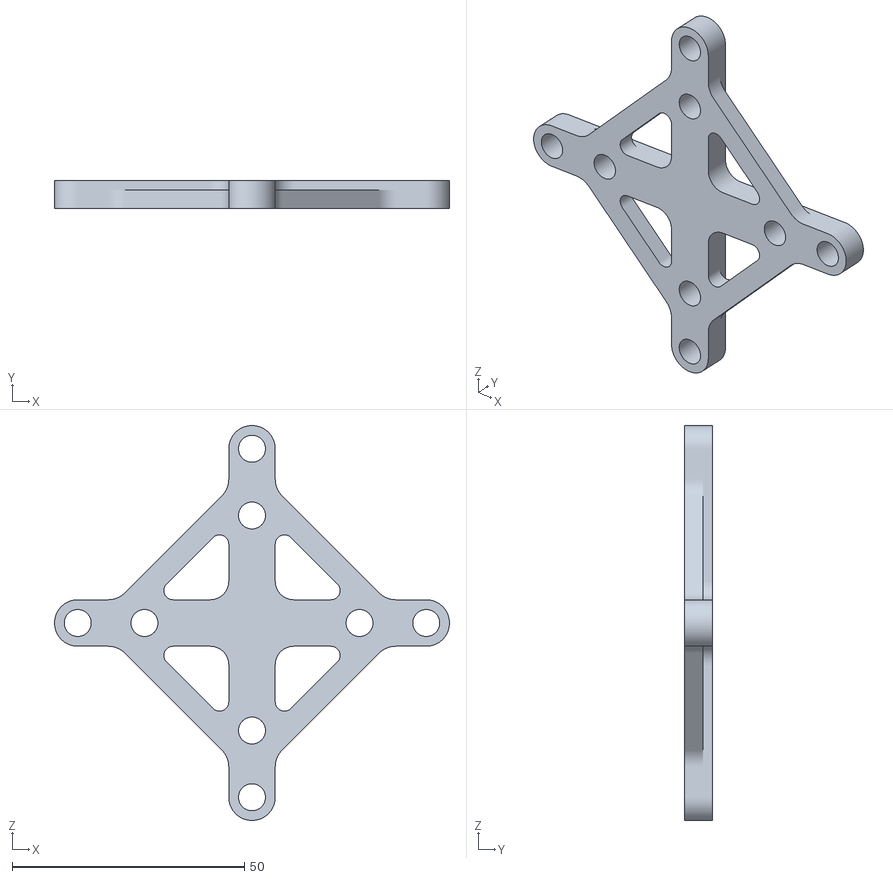
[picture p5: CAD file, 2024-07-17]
Main Assembly/Silicone Mold/CAD models/STL files/Assembly Cross.stl
85.0 x 6.00 x 85.0

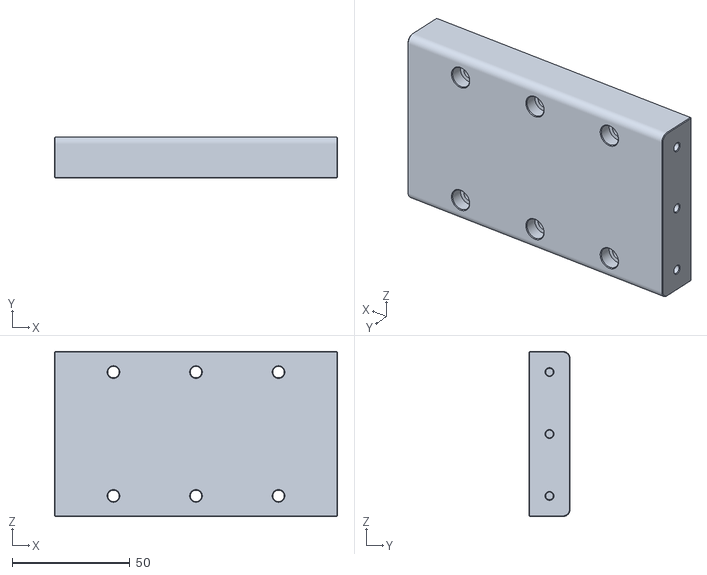
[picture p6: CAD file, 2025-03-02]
CAD/Square Silicone Rubber Mold/Main Center Mold Piece - Lid.stl
120.0 x 17.5 x 70.0

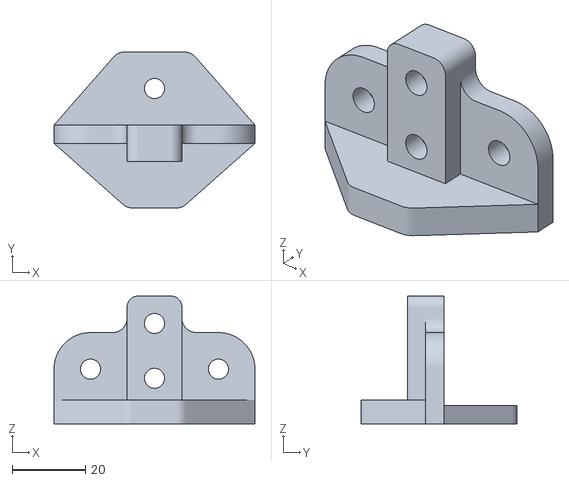
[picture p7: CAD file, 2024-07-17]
Actuators/Actuator V1 - Dual Motor Actuator/CAD models/STL files/Load Cell Mount V1.stl
55.0 x 42.7 x 35.0

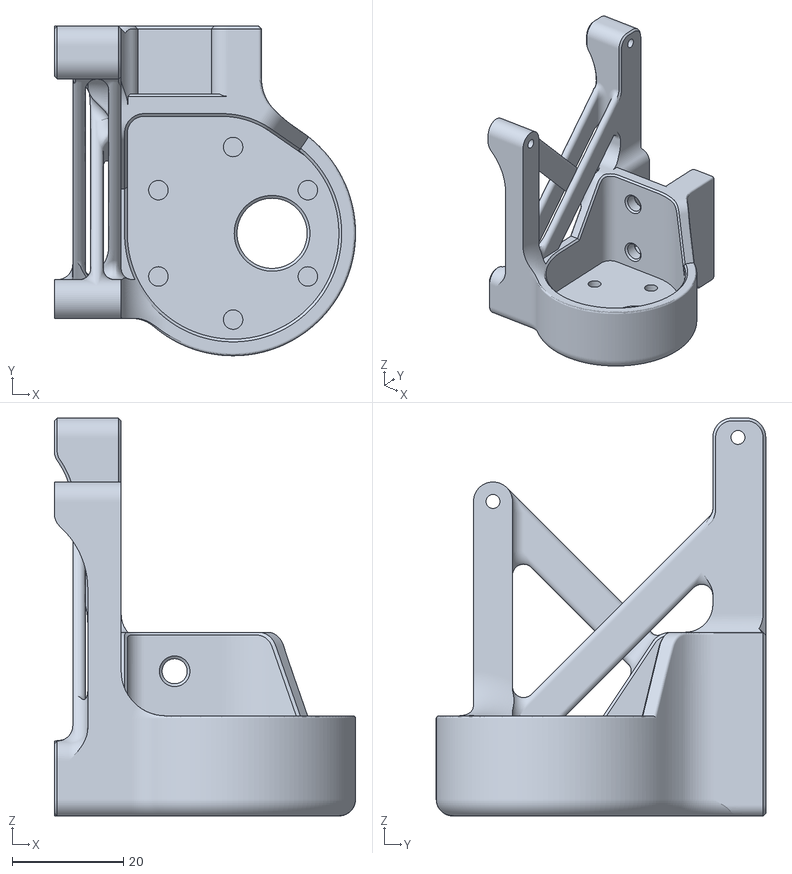
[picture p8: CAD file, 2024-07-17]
Actuators/Actuator V2/CAD models/STL Files/Motor Mount.stl
54.1 x 59.2 x 71.5

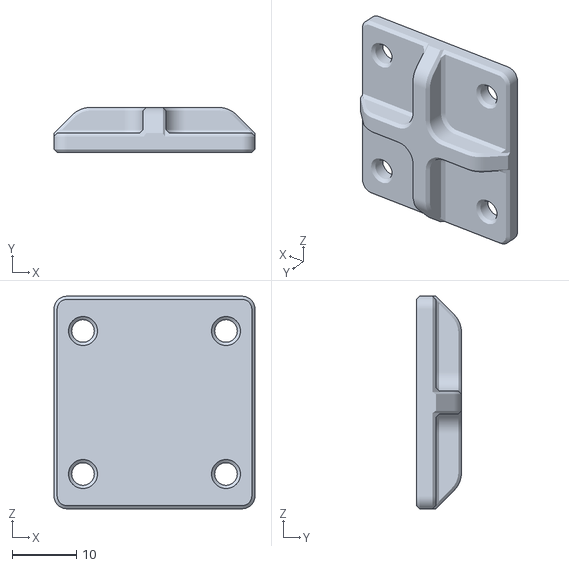
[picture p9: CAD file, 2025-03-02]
CAD/Actuator V2/Additional Motor Brace.stl
31.2 x 7.00 x 33.0

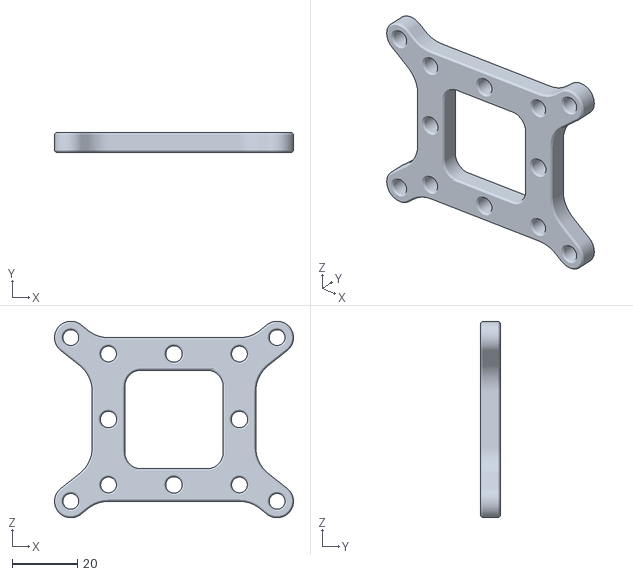
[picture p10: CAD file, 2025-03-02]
CAD/Round Silicone Rubber Mold/MoldPlateMount.stl
73.0 x 6.00 x 60.0

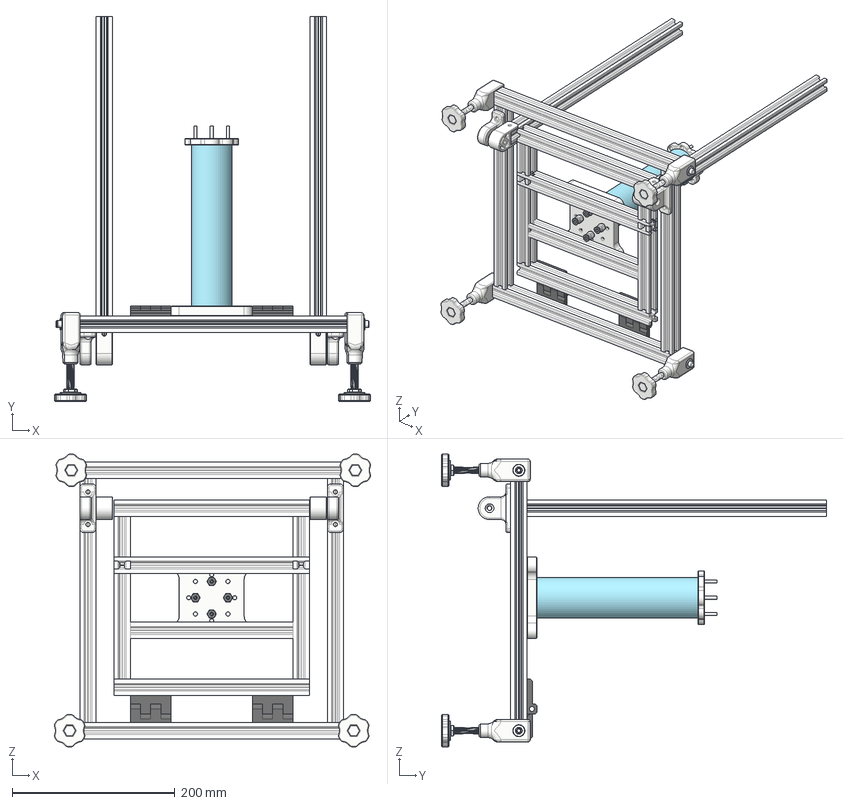
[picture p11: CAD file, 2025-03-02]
CAD/Soft Robot V2 v22.step
388.3 x 473.1 x 360.0 mm
Continuum Sillicone Cylinder
Universal Plate x 2
Cone Head Anchor x 8
Button Head Anchor x 10
M5 Nut x 8
PTFE Tubing x 8
Aluminium Extrusion 20x20 (2) x 2
Aluminium Extrusion 20x20 (3) (1)
Aluminium Extrusion 20x20 (3) x 3
M5x10mm x 8
Robot Mount V2
Full Motor Assembly V1.1_2
Full Motor Assembly V1.1_3
Hinge Part 2 x 2
Hinge Part 1 x 2
Aluminium Extrusion 20x20 (2) (1) x 2
M8 Screw x 4
M5 Washer x 4
M8 Washer x 4
UpperLeg x 4
M8 Nut x 4
M5 Screw x 4
Lower Leg x 4
Aluminium Extrusion 20x20 (2) (1) (1) x 2
Height Adjustable Profile Mount x 2
Aluminium Extrusion 20x20 (2) (2) x 2
Hinge for height adjuster x 2

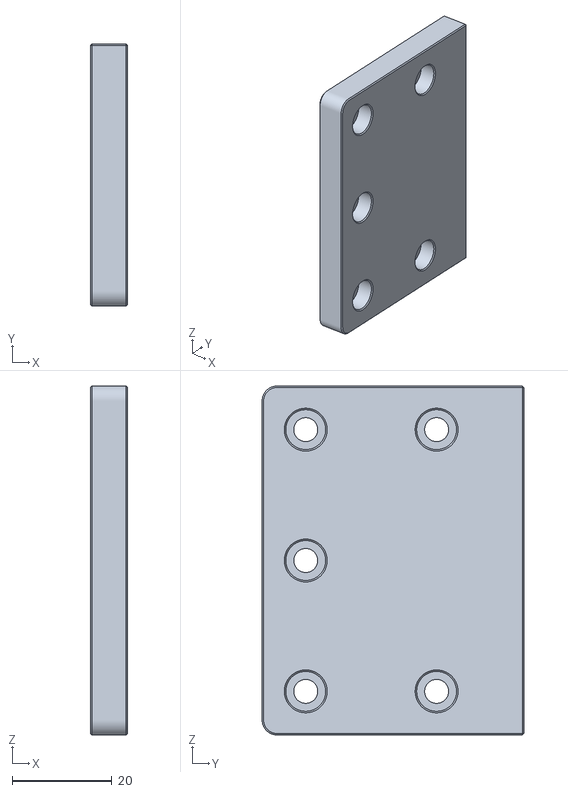
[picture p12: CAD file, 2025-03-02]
CAD/Square Silicone Rubber Mold/Simple End Cap.stl
7.50 x 52.5 x 70.0

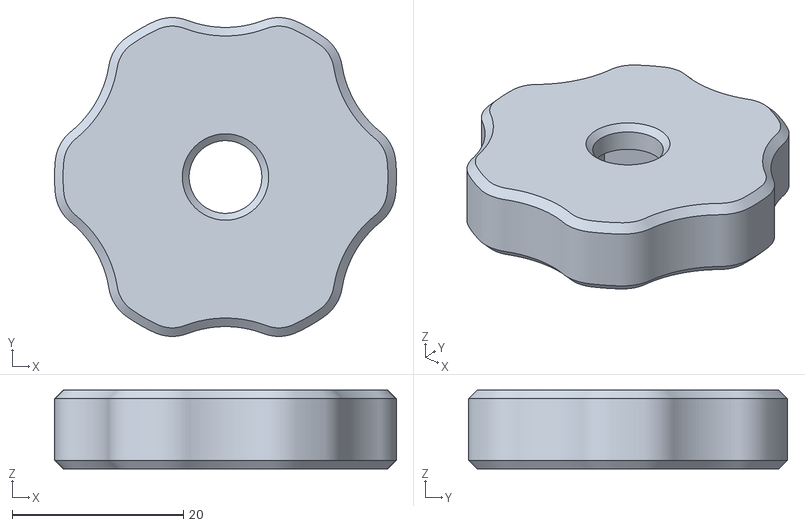
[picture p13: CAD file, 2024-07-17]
Main Assembly/Frame/CAD models/STL Files/Lower Leg.stl
40.0 x 37.3 x 9.20

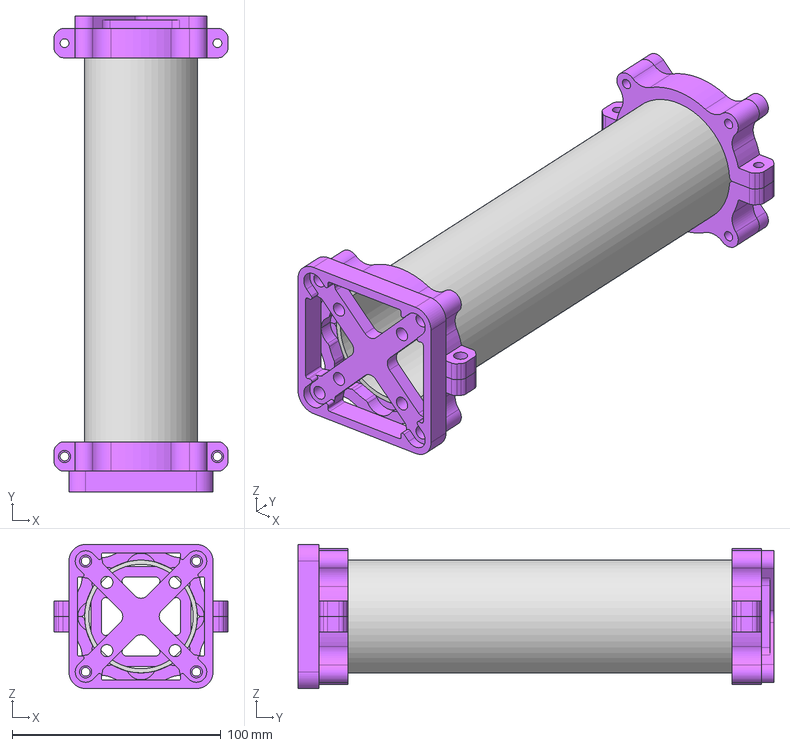
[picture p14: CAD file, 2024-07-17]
Main Assembly/Silicone Mold/CAD models/Full Assembly/Mold - V2.step
83.2 x 228.0 x 69.0 mm
Intact Pipe
Pipe Clamp 1 x 2
Pipe Clamp 2 x 2
Assembly Cross
Cross and Base

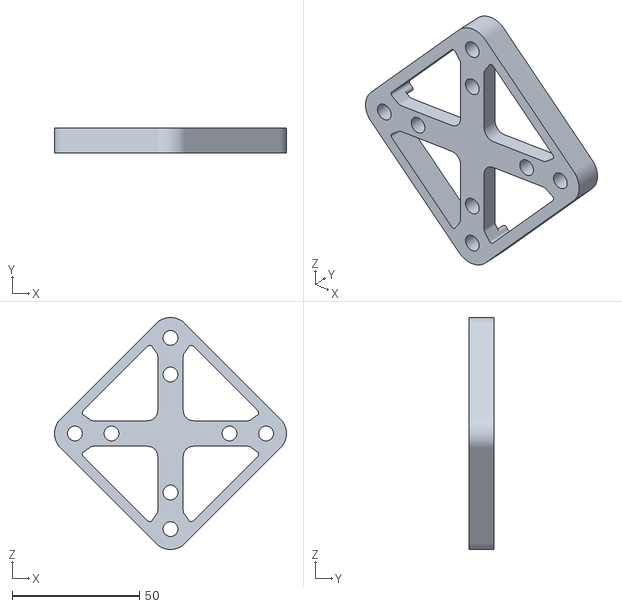
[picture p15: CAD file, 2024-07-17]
Main Assembly/Silicone Mold/CAD models/STL files/Cross and Base.stl
91.0 x 10.0 x 91.0

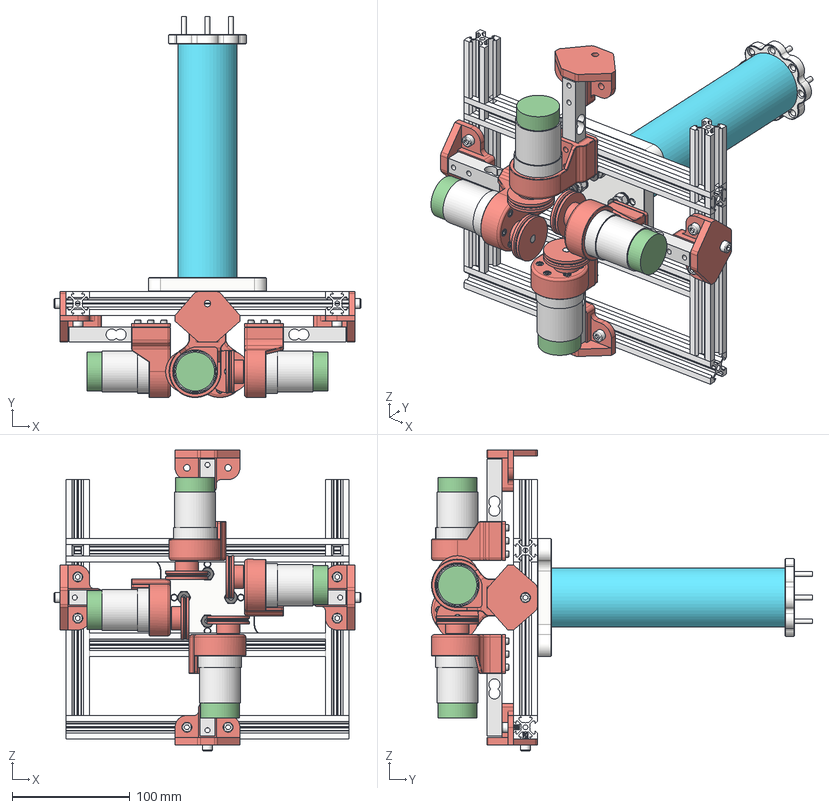
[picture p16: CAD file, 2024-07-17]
Main Assembly/Silicone Mounting/CAD models/Full Assembly/Soft Robot V1.step
260.0 x 323.1 x 255.0 mm
Continuum Sillicone Cylinder
Universal Plate x 2
Cone Head Anchor x 8
Button Head Anchor x 10
M5 Nut x 8
PTFE Tubing x 8
Aluminium Extrusion 20x20 (2) x 2
Aluminium Extrusion 20x20 (3) (1)
Aluminium Extrusion 20x20 (3) x 2
Robot Mount V2
Load Cell Mount V1 x 4
Pulley V1 x 4
M3x6mm x 48
Motor Mount x 4
Additional Motor Brace x 4
Load Cell x 4
Pololu 1442 Geared DC Motor x 4
M5x10mm x 21

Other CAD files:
Main Assembly/Silicone Mounting/CAD models/STL files/Robot Mount V2.stl
Test Stand/CAD Models - STL files/Spring Mount.stl
Actuators/Actuator V1 - Dual Motor Actuator/CAD models/STL files/Additional Motor Brace.stl
Actuators/Actuator V2/CAD models/STL Files/Pulley V1(Mirror).stl
Actuators/Actuator V1 - Dual Motor Actuator/CAD models/Full Assembly/Actuator V1.f3d
Actuators/Actuator V1 - Dual Motor Actuator/CAD models/STL files/Motor Mount.stl
Actuators/Actuator V1 - Dual Motor Actuator/CAD models/STL files/Pulley V1.stl
Actuators/Actuator V2/CAD models/STL Files/Load Cell Mount V1(Mirror).stl
Actuators/Actuator V2/CAD models/STL Files/Motor Cap V1.stl
CAD/Actuator V2/Load Cell Mount V2.stl
CAD/Actuator V2/Motor Cap V1.stl
CAD/Actuator V2/Motor Mount Mirrored with PCB.stl
CAD/Actuator V2/Small Pulley No Inserts.stl
CAD/Round Silicone Rubber Mold/MoldPipePart.stl
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

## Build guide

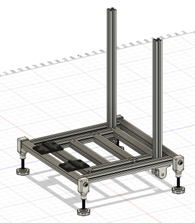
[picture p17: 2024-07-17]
Main Assembly/Frame/Pictures/FrameHorizontal.png

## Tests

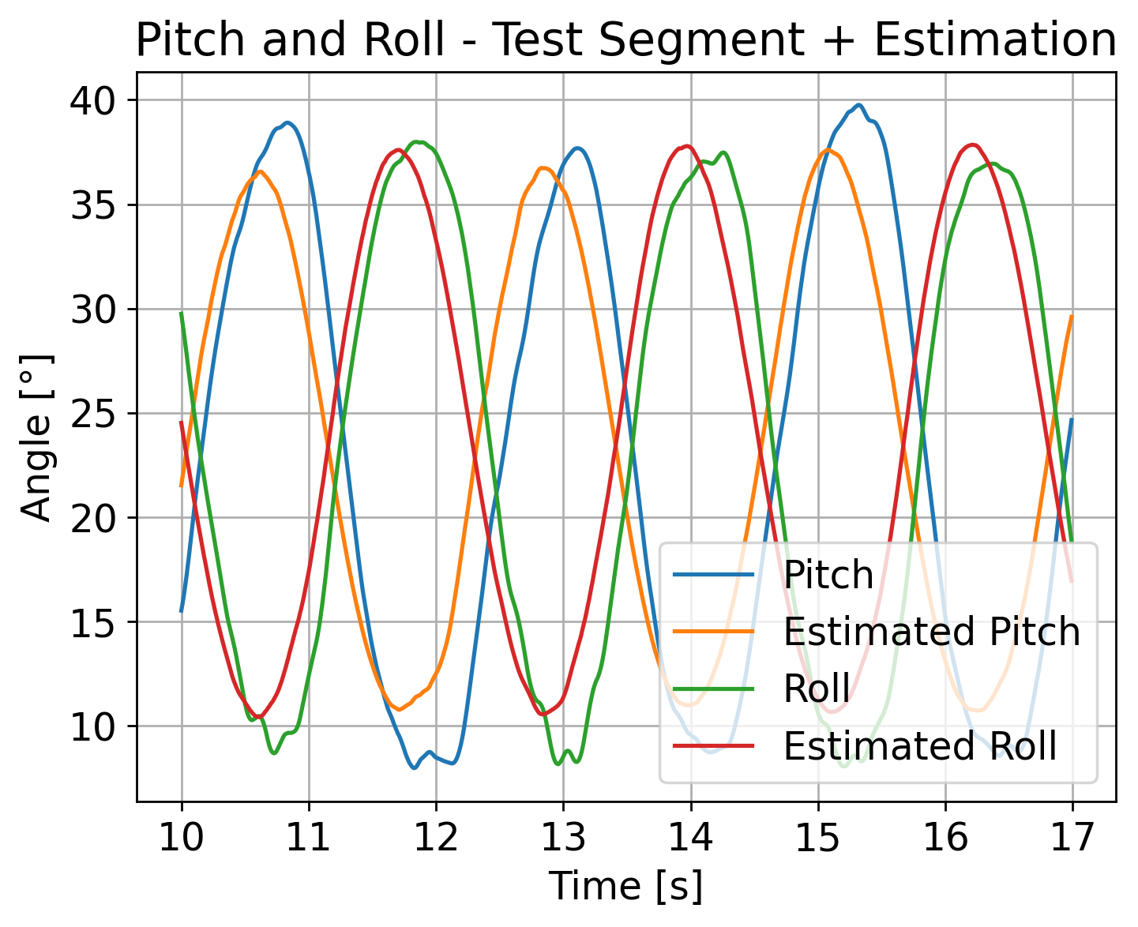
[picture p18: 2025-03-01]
Figures/Pitch and Roll - Test Segment + Estimation.png

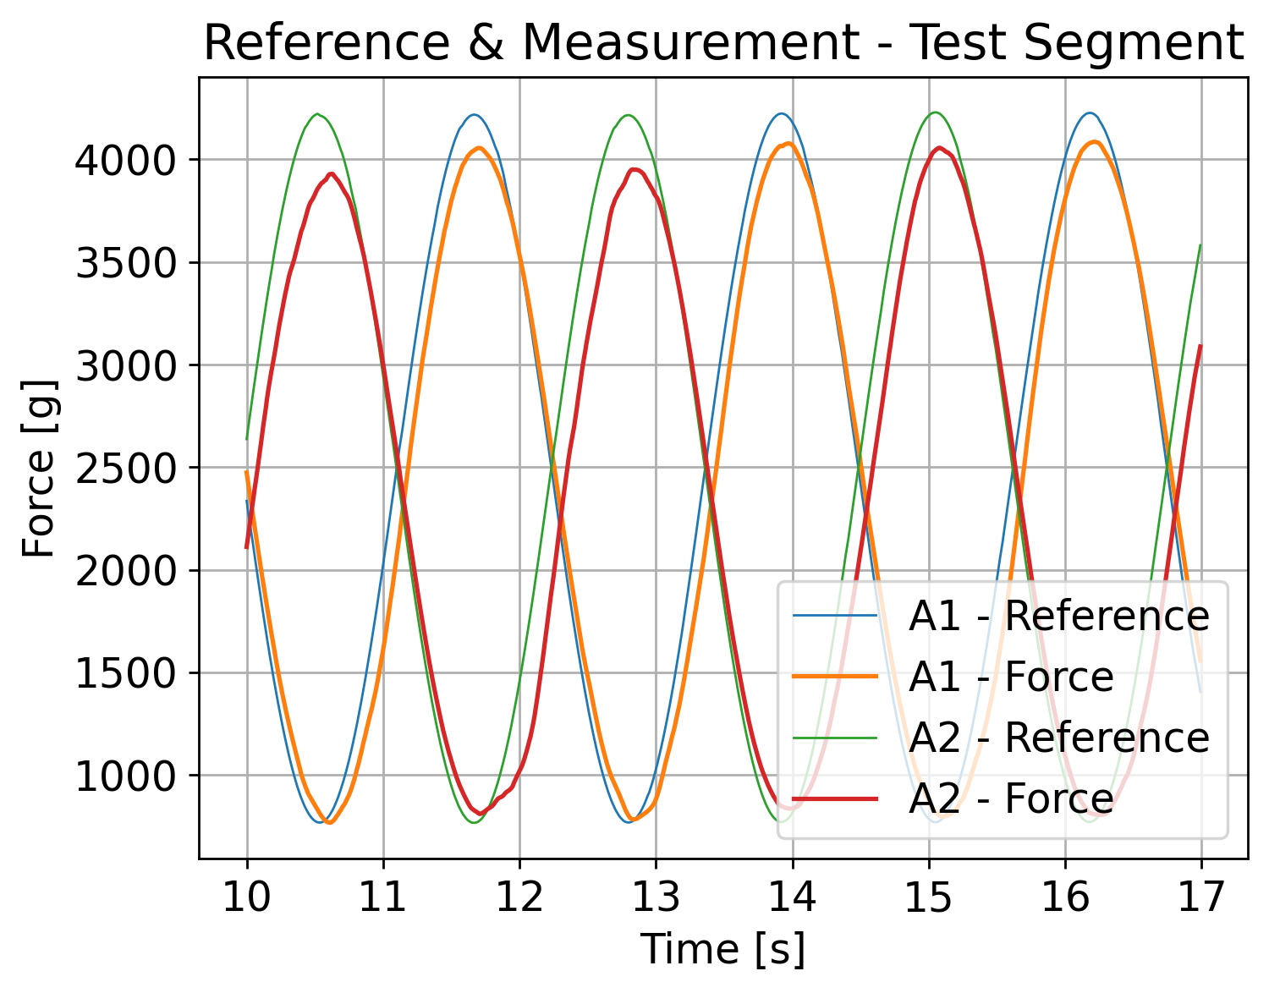
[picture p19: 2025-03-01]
Figures/Reference & Measurement - Test Segment.png

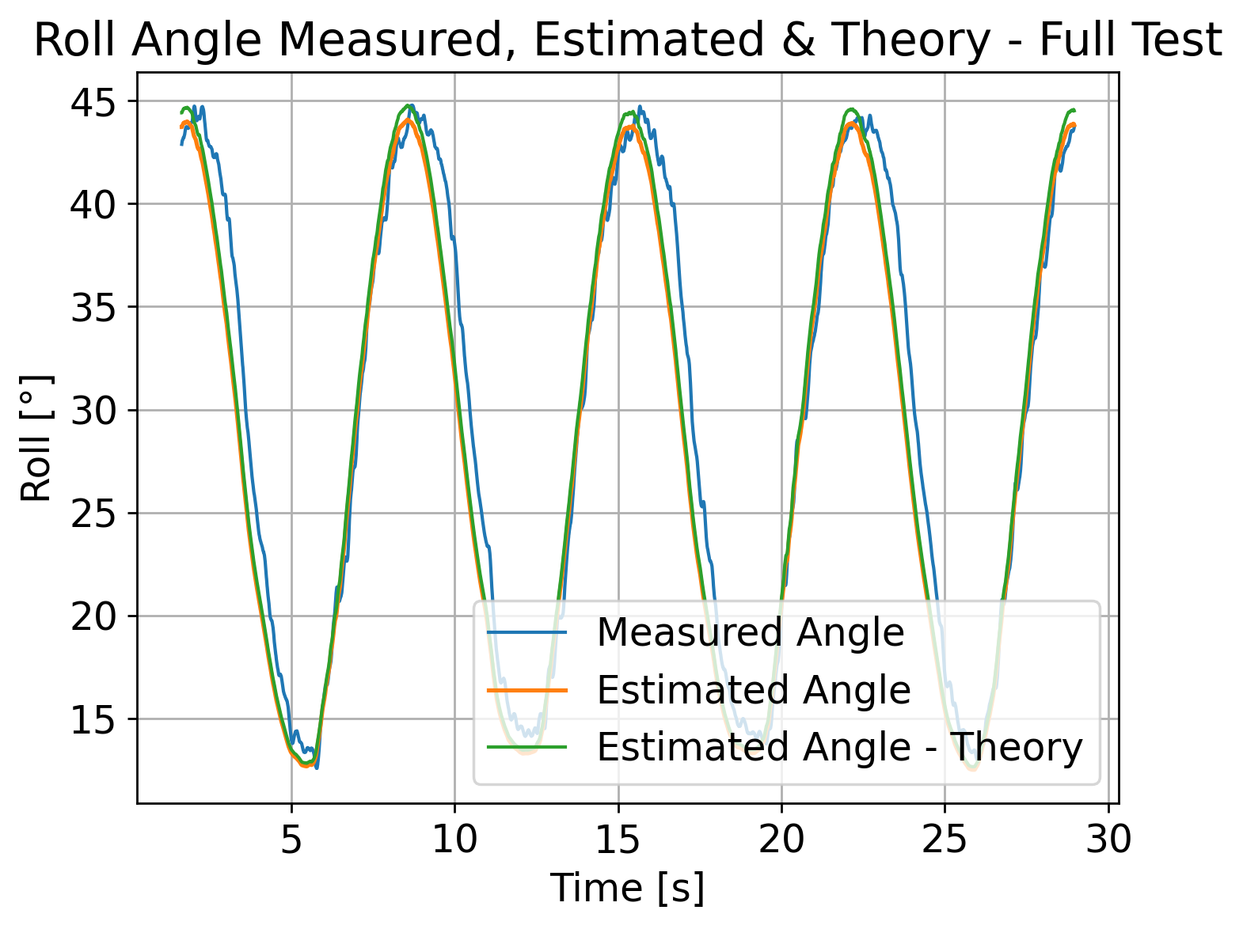
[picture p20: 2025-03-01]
Figures/Roll Angle Measured, Estimated & Theory - Full Test - Sine.png

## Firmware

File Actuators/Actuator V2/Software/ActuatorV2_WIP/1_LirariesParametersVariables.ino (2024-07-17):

/*
 *      LIBRARIES
 */
#include "RPi_Pico_TimerInterrupt.h"
#include "RP2040_PWM.h"
#include <Wire.h>

/*
 *      PINS
 */
#define PIN_MOTOR_PWM_1     2
#define PIN_DRV_DECAY       3
#define PIN_MOTOR_PWM_2     4
#define PIN_DRV_SLEEP       6
#define PIN_DRV_RESET       7
#define PIN_LED_HEARTBEAT   8
#define PIN_LED_FAULT       11
#define PIN_LED_ENABLE      12
#define PIN_LED_MODE        13
#define PIN_PICO_LED        25
#define PIN_MOTOR_CURR      26
#define PIN_INA125          27
#define PIN_INA826          28

/* 
 *      PARAMETERS 
 */
#define SERIAL_BAUDRATE     115200            // [9600/115200]  - Sets the baudrate of the Serial connection
#define SERIAL_DEBUG        false              // [true / false] - Enables / Disables the Serial debug output
#define STARTSEQ_WAIT       300               // [ms]           - Determines the speed of the LED Start Sequence
#define PERIOD_TIMER_LED    100000            // [us]           - Number of microseconds a period of the timer lasts
#define PERIOD_TIMER_COM    1000              // [us]           - Number of microseconds a period of the timer lasts
#define PERIOD_TIMER_CTRL   500               // [us]           - Number of microseconds a period of the timer lasts
#define PERIOD_TIMER_SEN    500               // [us]           - Number of microseconds a period of the timer lasts
#define LEN                 16                // [b]            - Number of bits 
#define PWM_FREQUENCY       5000              // [Hz]           - PWM Frequency in Hertz
#define DATA_STREAM_LEN     12                // [#]            - Number of different data points collected by the actuator
#define INA826_K            2.2629            // [#]            - K from the calibration procedure for the INA826
#define INA826_N            1.33955           // [#]            - N from the calibration procedure for the INA826
#define ALGORITHM           2                 // [#]            - Number of the algorithm selected for the control of the actuator

// Controller Parameters & Variables
// Parameters
#define MIN_REFERENCE       0.00              // [g]            - Minimum reference that can be sent to the controller
#define MAX_REFERENCE       5000.00           // [g]            - Maximum reference that can be sent to the controller
#define MIN_OUTPUT          -100.00           // [%]            - Minimum duty cycle as the output of the controller
#define MAX_OUTPUT          100.00            // [%]            - Maximum duty cycle as the output of the controller
#define KP                  0.08              // [#]            - Kp value for the PI controller
#define KI                  0.00002           // [#]            - Ki value for the PI controller
#define ACC_MAX             1000


// Variables
volatile float reference    = 0.00;           // [g]            - Reference for the PI controller
volatile float acc          = 0.00;           // [g]            - Accumulator for the PI controller
volatile float e            = 0.00;           // [g]            - Error for the PI controller
volatile float pi_duty      = 0.00;           // [%]            - Calculated duty cycle as the output of the PI controller
volatile int   pi_dir       = 1;              // [1/2]          - Motor spinning direction based on the output of the PI controller

#define KP_BASE             0.0009              // [#]            - Base value for the KP2
#define DIR_UP              2.0               // [#]            - Direction factor for tensioning the string
#define DIR_DOWN            0.8               // [#]            - Direction factor for tensioning the 
#define FF                  0.00002            // [#]            - Force factor correction parameter
#define KD_BASE             0.9              // [#]            - Base value for the KD2
#define DF                  1.2               // [#]            - Derivative control factor for adjusting the variable part of the KP2    
#define KPROX               10                 // [#]            - Proximity correction factor for the PD controller
#define PIR                 150               // [g]            - Range for the PI controller
#define PDR                 1000              // [g]            - Range for the PD controller

// Variables for algorithm 2
volatile float last_e       = 0.00;           // [g]            - Error in the last loop iteration for the controller
volatile float KP2          = KP_BASE;        // [#]            - Kp value for the controller of the Algorithm 2
volatile float KD2          = KD_BASE;        // [#]            - Kd value for the controller of the Algorithm 2
volatile bool  last_pi      = false;          // [true/false]   - Flag for figuring out if the last controller was PI or not
volatile float KDIR2        = 0.00;           // [#]            - Direction factor used in the second algorithm

/*
 *      VARIABLES 
 */
bool error                  = false;          // Flag that tells us if we have an erro in our system
int led_skip                = 0;              // Flag for skipping turning on the built in LED
int led_state               = 1;              // Built in LED status
volatile bool new_message   = false;          // Flag for checking if there are any new messages
volatile bool new_command   = false;          // Flag that indicates if there is a new command present that needs to be processed
String serial_msg           = "";             // String for holding the Serial message
volatile byte i2c_msg[LEN]  = {};             // Variable (array) for holding the byte array which is the I2C message
volatile bool driver_enable = false;          // Flag for holding the information if the driver should be enabled or not
int decay_mode              = 0;              // Variable for holding the current decay mode, 1 - Fast Decay, 0 - Slow Decay
int CONTROLLER_MODE         = 1;              // Variable for configuring in what mode the controller is, 1 - Manual, 2 - Load Cell PI, 3 - IMU PI
int mode_led_skip           = 0;              // Flag for skipping turning on the Mode LED
int mode_led_state          = 1;              // Mode LED status
volatile int current_dir    = 1;              // The current direction in which the motor is spinning
volatile int current_duty   = 0;              // The current desired duty cycle of the PWM
bool serial_data_stream     = false;          // Flag that controls the serial data stream
volatile int motor_current  = 0;              // Variable for keeping the raw data from the ADC connected to the current measuring of the DRV8842
volatile int ina125         = 0;              // Variable for keeping the raw data from the ADC connected to the INA125 amplifier
volatile int ina826         = 0;              // Variable for keeping the raw data from the ADC connector to the INA826 amplifier
volatile float ina826g      = 0;              // Variable for keeping the calculated weight from the INA826
volatile int data_flag      = 0;

/*
 *  Data stream variable - array of numbers
 *  0  - Actuator ID
 *  1  - Current Reading
 *  2  - INA826 Reading
 *  3  - INA125 Reading
 *  4  - PWM Reading 1     - TODO
 *  5  - PWM Reading 2     - TODO
 *  6  - Encoder A         - TODO
 *  7  - Encoder B         - TODO
 *  8  - Actuator Mode     - TODO
 *  9  - Driver Fault      - TODO
 *  10 - Driver Enable     - TODO
 *  11 - Actuator Error    - TODO
 */
volatile int data_stream[DATA_STREAM_LEN] = {};

/*
 *      TIMERS 
 */
RPI_PICO_Timer              TimerLED(0);      // Timer for the heartbeat LED                          - Frequency set in setup() - Default 10 Hz
RPI_PICO_Timer              TimerCOM(1);      // Timer for setting the communication rate             - Frequency set in setup() - Default 1 kHz
RPI_PICO_Timer              TimerCTRL(2);     // Timer for controlling the motor, both manual and PI  - Frequency set in setup() - Default 2 kHz
RPI_PICO_Timer              TimerSEN(3);      // Timer for sensor data acqusition                     - Frequency set in setup() - Default 2 kHz

/*
 *      PWM
 */
RP2040_PWM*                 PWM_Instance[2];  // PWM for the Pico

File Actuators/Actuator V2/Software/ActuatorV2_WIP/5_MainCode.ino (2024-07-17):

void setup() {
  // Setting up Serial Communication
  Serial.begin(SERIAL_BAUDRATE);
  sprintln("Actuator V2 has started!");

  // Setting up all of the pins
  // Motor Pins
  pinMode(PIN_MOTOR_PWM_1,    OUTPUT);
  pinMode(PIN_MOTOR_PWM_2,    OUTPUT);
  // LED Pins
  pinMode(PIN_LED_HEARTBEAT,  OUTPUT);
  pinMode(PIN_LED_FAULT,      OUTPUT);
  pinMode(PIN_LED_ENABLE,     OUTPUT);
  pinMode(PIN_LED_MODE,       OUTPUT);
  // DRV Control Pins
  pinMode(PIN_DRV_RESET,      OUTPUT);
  pinMode(PIN_DRV_SLEEP,      OUTPUT);
  pinMode(PIN_DRV_DECAY,      OUTPUT);
  // Analog Pins
  pinMode(PIN_MOTOR_CURR,     INPUT);
  pinMode(PIN_INA125,         INPUT);
  pinMode(PIN_INA826,         INPUT);

  // Setting the initial pin state for the LED-s
  digitalWrite(PIN_LED_HEARTBEAT, HIGH);
  digitalWrite(PIN_LED_FAULT,     HIGH);
  digitalWrite(PIN_LED_ENABLE,    HIGH);
  digitalWrite(PIN_LED_MODE,      HIGH);

  // Setting the Analog Read Resolution
  analogReadResolution(12);

  // Run the LED Start Sequence
  StartSequence();

  // Disable the driver
  UpdateDriver(driver_enable);

  // Set the default decay mode
  DecayMode(decay_mode);

  // Setting up Timers
  
  // LED Timer - Frequency set in the Parameters section
  if (TimerLED.attachInterruptInterval(PERIOD_TIMER_LED, HeartbeatLEDHandler))
  {
    sprint("Starting LED Timer OK, millis() = ");
    sprintln(String(millis()));
  }
  else
    sprintln("Can't set LED Timer. Select another freq. or timer");

  // COM Timer (Communication) - Frequency set in the Parameters section
  if (TimerCOM.attachInterruptInterval(PERIOD_TIMER_COM, CommunicationHandler))
  {
    sprint("Starting COM Timer OK, millis() = ");
    sprintln(String(millis()));
  }
  else
    sprintln("Can't set COM Timer. Select another freq. or timer");

  // CTRL Timer (Control) - Frequency set in the Parameters section
  if (TimerCTRL.attachInterruptInterval(PERIOD_TIMER_CTRL, ControlHandler))
  {
    sprint("Starting CTRL Timer OK, millis() = ");
    sprintln(String(millis()));
  }
  else
    sprintln("Can't set CTRL Timer. Select another freq. or timer");

  // SEN Timer (Sense) - Frequency set in the Parameters section
  if (TimerSEN.attachInterruptInterval(PERIOD_TIMER_SEN, SenHandler))
  {
    sprint("Starting SEN Timer OK, millis() = ");
    sprintln(String(millis()));
  }
  else
    sprintln("Can't set CTRL Timer. Select another freq. or timer");

  // Setting up PWM
  PWM_Instance[0] = new RP2040_PWM(PIN_MOTOR_PWM_1, PWM_FREQUENCY, 0.00f);
  PWM_Instance[0]->setPWM();
  PWM_Instance[1] = new RP2040_PWM(PIN_MOTOR_PWM_2, PWM_FREQUENCY, 0.00f);
  PWM_Instance[1]->setPWM();
}

void loop() {
  
}

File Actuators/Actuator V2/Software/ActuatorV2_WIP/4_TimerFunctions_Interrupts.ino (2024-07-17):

/*
 *      LED TIMER
 */
bool HeartbeatLEDHandler(struct repeating_timer *t)
{
  (void) t;
  // Heartbeat LED
  if(error == true)
  {
    // If we're in error mode, we don't do a skip, we toggle the LED with every timer call
    if(led_state == 1)  digitalWrite(PIN_PICO_LED, HIGH);
    if(led_state == -1) digitalWrite(PIN_PICO_LED, LOW);
    if(led_state == 1)  digitalWrite(PIN_LED_HEARTBEAT, HIGH);
    if(led_state == -1) digitalWrite(PIN_LED_HEARTBEAT, LOW);
    led_state = -1 * led_state;
  }
  else
  {
    // If we're not in error mode, we need to skip every other toggle
    if(led_skip == 10)
    {
      if(led_state == 1)  digitalWrite(PIN_PICO_LED, HIGH);
      if(led_state == -1) digitalWrite(PIN_PICO_LED, LOW);
      if(led_state == 1)  digitalWrite(PIN_LED_HEARTBEAT, HIGH);
      if(led_state == -1) digitalWrite(PIN_LED_HEARTBEAT, LOW);
      led_state = -1 * led_state;
      led_skip = 0;
    }
    else
    {
      led_skip++;
    }
  }

  // Mode LED
  if(CONTROLLER_MODE == 3)
  {
    if(mode_led_state == -1)  digitalWrite(PIN_LED_MODE, HIGH);
    if(mode_led_state == 1) digitalWrite(PIN_LED_MODE, LOW);
    mode_led_state = -1 * mode_led_state;
  }
  else if (CONTROLLER_MODE == 1)
  {
    // If we're not in error mode, we need to skip every other toggle
    if(mode_led_skip >= 10)
    {
      if(mode_led_state == -1)  digitalWrite(PIN_LED_MODE, HIGH);
      if(mode_led_state == 1) digitalWrite(PIN_LED_MODE, LOW);
      mode_led_state = -1 * mode_led_state;
      mode_led_skip = 0;
    }
    else
    {
      mode_led_skip++;
    }
  }
  else if (CONTROLLER_MODE == 2)
  {
    if(mode_led_state == -1)  digitalWrite(PIN_LED_MODE, HIGH);
    if(mode_led_state == 1) digitalWrite(PIN_LED_MODE, LOW);
  }
  /*
  // Serial data stream
  if (serial_data_stream == true)
  {
    PrintDataStream();
  }*/
  
  return true;
}

/*
 *      COM TIMER 
 */
bool CommunicationHandler(struct repeating_timer *t)
{
  (void) t;
  
  // Check if there are any commands that need to be executed
  if (new_command == true)
  {
    new_command = false;
    switch(i2c_msg[0])
    {
      case 1:
      {
        // Command C1 - Enable/Disable driver
        if (i2c_msg[1] == 1)
        {
          sprintln("Received command C1 to Enable Driver.");
          sprintln("Pink LED should turn ON.");
          driver_enable = true;
        }
        else
        {
          sprintln("Received command C1 to Disable Driver.");
          sprintln("Pink LED should turn OFF");
          driver_enable = false;
        }
        UpdateDriver(driver_enable);
        break;
      }
      case 2:
      {
        // Command C2 - Change Decay Mode
        if (i2c_msg[1] == 1)
        {
          sprintln("Switching to Fast Decay mode.");
          decay_mode = 1;
        }
        else
        {
          sprintln("Switching to Slow Decay mode.");
          decay_mode = 0;
        }
        DecayMode(decay_mode);
        break;
      }
      case 3:
      {
        // Command C3 - Change Controller Mode
        // Mode 1 - Manual Control Mode
        // Mode 2 - Load Cell PI Mode
        // Mode 3 - IMU PI Mode
        if (i2c_msg[1] == 1)
        {
          sprintln("Switching to Mode 1.");
          CONTROLLER_MODE = 1;
        }
        else if (i2c_msg[1] == 2)
        {
          sprintln("Switching to Mode 2.");
          mode_led_state  = -1;
          CONTROLLER_MODE = 2;
        }
        else if (i2c_msg[1] == 3)
        {
          sprintln("Switching to Mode 3.");
          CONTROLLER_MODE = 3;
        }
        break;
      }
      case 4:
      {
        // Command C4 - Manual PWM control
        // Updating the direction
        if (i2c_msg[1] != 3)
        {
          current_dir = i2c_msg[1];
        }
        // Updating the speed
        current_duty = i2c_msg[2];
        // Sending the command to the motor driver
        sprintln("Sending new PWM command to the motor driver.");
        MotorDriver(current_dir, current_duty);
        break;
      }
      case 5:
      {
        sprintln("Received command for updating the PI controller reference");
        reference = i2c_msg[1] * 255 + i2c_msg[2];
        sprint("Requested reference: ");
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

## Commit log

2025-03-01 mold picture added
2025-03-02 CAD Files Upload
    [Additional Motor Brace.stl, Conitnuum Cap Test V1.stl, Conitnuum Cap V2.stl, Load Cell Mount V2.stl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]
